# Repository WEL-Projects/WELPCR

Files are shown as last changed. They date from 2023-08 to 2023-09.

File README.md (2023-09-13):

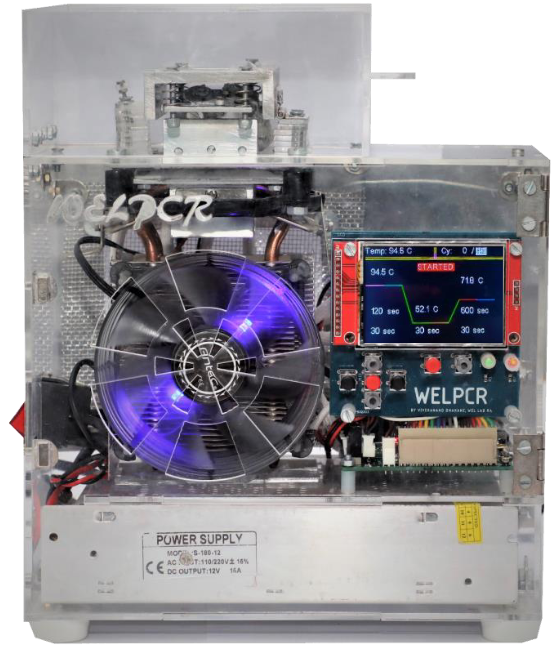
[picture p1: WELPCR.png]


# WELPCR
WELPCR is a low-cost polymerase chain reaction (PCR) thermal cycler for DNA amplification, developed at the [Wadhwani Electronics Lab (WEL)](https://www.ee.iitb.ac.in/~wel_iitb/), [IIT Bombay](https://www.iitb.ac.in/). It is inspired by the [OpenPCR](https://openpcr.org/) design and is a standalone device which does not require connection to a computer or a mobile device for configuration and operation. The bill of materials (BOM) cost for assembling one unit of WELPCR is less than INR Rs. 10,000 (approximately USD $120), which makes it a great resource for educational and research use in laboratories with limited resources. The WELPCR design is open-source and made available for developers interested in assembling their own units.

WELPCR YouTube video: [Watch video](https://www.youtube.com/watch?v=7obOnxuG-sw)

Media article on WELPCR: [Read article](https://www.thehindubusinessline.com/business-tech/affordable-pcr-testing/article65438612.ece)

**If you use this documentation for your project, please cite WELPCR:**

Poulami Mandal*, Vivekanand Dhakane*, Avani Kulkarni, Siddharth Tallur, "WELPCR: Low-cost polymerase chain reaction (PCR) thermal cycler for nucleic acid amplification and sensing," bioRxiv 2023.09.11.557292 (2023). (*equal contribution)

doi: [https://doi.org/10.1101/2023.09.11.557292](https://www.biorxiv.org/content/10.1101/2023.09.11.557292v1)

## Files and folders index
### Folders
Mechanical_design_files: 3D drawings and design files to build the mechanical assembly

PCB: PCB schematic and gerber files for PCR motherboard and display board

STM32_PCR_firmware_for_WELPCR: Firmware for STM32 microcontroller

### Files
Assembly_Instruction.pdf: Step by step guide for assembling WELPCR

MTP PPT.pdf: M.Tech. thesis presentation by Mr. Vivekanand Dhakane

MTP_Report.pdf: M.Tech. thesis report by Mr. Vivekanand Dhakane

Validation document WELPCR.pdf: Protocols for operating WELPCR

WELPCR.png: Photograph of fully assembled WELPCR machine

WELPCR_Temperature_Protocol.pdf: Temperature profile for WELPCR for 16s universal primers

WEL_PCR_BOM.xlsx: Bill of materials (BOM) for WELPCR

WEL_PCR_User_manual.pdf: User manual for operating WELPCR

## Credits
Design and development: Vivekanand Dhakane

Testing and validation: Avani Kulkarni

Documentation and training: Poulami Mandal

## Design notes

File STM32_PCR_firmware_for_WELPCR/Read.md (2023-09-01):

Download stm32 cube ide version 1.6.1
This file[en.st-stm32cubeide_1.6.1_9958_20210326_1446_x86_64.exe]

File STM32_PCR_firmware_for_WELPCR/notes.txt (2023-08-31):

*For lid heater it is found that when PWM 35% then temp is constant at 100 degree
current was nearly 0.85A

*when mosfet is driven by 3.3v
	temperature set =50 degree
		
		if fan not turned on heat sink .its temp = 80
		if fan turned on heat sink .its temp = 56

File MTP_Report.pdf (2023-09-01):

# Low-cost electrochemical sensing

# platform for DNA analysis

### M.Tech Thesis

Submitted in partial fulfillment of the requirements for the degree of

Master of Technology
Solid State Devices (EE7)

by

### Vivekanand Ramrao Dhakane

(193079041)

Under the guidance of

### Prof. Siddharth Tallur

Department of Electrical Engineering, Indian Institute of Technology - Bombay, Powai, Bombay 400076.
June, 2022.

# Thesis Approval

The Thesis entitled

### Low-cost electrochemical sensing platform for DNA analysis

by

Vivekanand Ramrao Dhakane
(193079041)

is approved for the degree of Master’s of Technology in the Department of Electrical Engineering

Prof. Siddharth Tallur
Department of Electrical Engineering (Supervisor)
Prof. Mukul Chandorkar | Prof. Swaroop Ganguly
Department of Electrical Engineering | Department of Electrical Engineering
(Examiner/Chairperson) | (Examiner)

Prof. Debjani Paul
Department of Biosciences and Bioengineering (Examiner)

Date: June 29, 2022
Place: Mumbai.

ii

# Declaration

I declare that this written submission represents my ideas in my own words, and where other ideas or words have been included, I have adequately cited and referenced the original sources. I also declare that I have adhered to all principles of academic honesty and integrity and have not misrepresented, fabricated, or falsified any idea/data/fact/source in my submission. I understand that any violation of the above will cause disciplinary action by the Institute or from whom proper permission has not been taken when needed.

Vivekanand Ramrao Dhakane
(193079041)

June 29, 2022

iii

# Acknowledgement

First and foremost, I am extremely grateful to Prof. Siddharth Tallur for his invaluable advice, continuous support, and patience throughout this project. I am grateful for the constant support and immense help from Maheshwar Mangat Sir in circuit and PCB designing and Mahesh Bhaganagare Sir for helping me in purchasing, and issuing the components from the WEL lab. I am thankful to my colleagues Ruchira Nandeshwar and Shruti Ahuja for their help during the testing of WELStat and Avani Kulkarni for the testing of WELPCR. I would like to thank Mr Vishwas Kewle, Senior Mechanic in Machine tools lab, Mechanical dept for fabricating the heat block and aluminum bracket. I would also like to thank Rutuja Chalke, illustrator in the WEL lab to help me with the PCR illustrations. I would like to express my sincere gratitude to WEL lab authorities for allowing me to use their facilities. I appreciate the constant support from the WEL lab staff, Sadanand sir, Suraj sir, Amit sir, Shanin sir, Shekhar sir and Varsha ma’am. I always had project related brainstorming with my friends Saurabh Thakur, Sarvesh Kale, Omkar Phadke and Jay Jadhav. Finally, I am forever grateful for the encouragement, patience, and support from my parents. Without their tremendous understanding in the past few years, it would be impossible for me to complete this project. I could not have done any of this without them. Thank you all.

Vivekanand Ramrao Dhakane
(193079041)

iv

# Abstract

The ongoing COVID-19 pandemic has highlighted the need for sensitive and cost-effective diagnostics. The gold standard test to diagnose COVID-19 is real time PCR and although there have been multiple advances in PCR testing, the real time PCR thermocyclers are bulky and expensive. Given that PCR is one of the most sensitive and specific testing methods for diagnosis, it is necessary to find a solution to make it affordable especially for low middle income countries(LMICS). This led to the objective of this project to develop a low-cost, portable, and automated real time PCR device. This project includes WELPCR (portable thermocycler), and WELStat (potentiostat that can be connected to a smartphone for electrochemical measurements). The user has to add PCR master mix to pre-processed samples and place them in the holder on WELPCR. The temperature profile and other parameters can be visualized on the LCD display. An electroless nickel immersion (ENIG) PCB electrode is immersed in the PCR sample tubes to note the electrochemical measurements for real-time quantification.

v

# Contents

1 Introduction | 1
2 WELPCR | 4
3 WELStat 2.0 | 22
3.8.1 | End point PCR testing using WELPCR + WELStat . . . . | 32
Appendices | 36

vi

A WELPCR User Manual | 36
B Design Files | 40

vii

# List of Figures

2.4 (a) WELPCR designed in CAD tool Autodesk fusion 360 (b) Actual

2.6 (a) Raw Aluminium block (b) Tube holder after manufacturing (c) bracket after manufacturing (d) Eppendorf tube (e) modified drill bit 8 2.7 (a) 2D parts in WELPCR (b) 2mm aluminium sheet under laser

2.10 (a) Proportional and controller derivative, (b) PD vs PID controller,
(c) Removal of overshoot to get final PID controls, (d) PCR temper-

2.11 Plot showing temperature difference between tube holder and sample 15 2.12 (a) Insulation layer (VHB tape) applied on the tube holder (b) Plot

2.13 (a) Nichrome heater (b) Internal structure of Nichrome heater . . . 16 2.14 (a) Condensation observed in 0.5ml tubes, (b) Tubeholder redesigned

2.15 Comparison of time response for 1mm, 2mm and 5mm thermistor . 17 2.16 (a) Thermistor connected in voltage divider, (b)Set-up for calibrating

viii

2.18 Agarose gel showing 503bp fragment of bacteriophage Phi6 after 35 cycles amplified using WELPCR. NTC is the negative sample and
PC is the positive sample | 19
2.19 Current vs number of cycles plot showing decrease in current with
increase in cycles. Inset showing micro-electrode inserted in the tube | 20
3.1 Working of the Potentiostat, case-I, case-II, and case-III | | 23
3.2 (a) WELSTAT designed in Computer Aided Design tool Autodesk
Fusion 360, (b) WELSTAT after manufacturing | 24
3.3 (a) AD5941, (b) functional block diagram of AD5941 (taken from its
datasheet | 25
3.4 (a)Testing AD5941 on evaluation board, (b) Cyclic Voltammetry plot
for 50µM Methylene blue on AD5941 Evaluation-board | | 26
3.5 STM32F103C8PC IC | | 26
3.6 First PCB for testing minimal circuit for AD5941 | | 27
3.7 Second PCB with both AFE and micro-controller on same board . . | 28
3.8 WELStat software GUI | | 28
3.9 (a)USB wire touching the the electrode wire, (b) Using long wire to connect the electrode, (c) connecting electrode on PCB, (d) IV plot
for 1Mohm when USB wire was touching the the electrode wire (e)
IV plot for 1Mohm when long wire was used to connect the electrode,
(f) IV plot for 1Mohm when electrode was directly connected on PCB 32 3.10 Cyclic voltammetry plot for different concentrations of Methylene
Blue | 33
3.11 Cyclic voltammetry plot for 503bp fragment of Phi6 amplified after 35 cycles using WELPCR and electrochemically detected using WELSTAT. NC is the no-template control, PC is the positive control 33
3.12 H-brige using 4 discrete MOSFET and VNH2SP30 IC | | 35
A.1 (a)PCR parameter window, (b) PCR parameter monitor window . . | 36
A.2 Details about the PCR parameter window | | 37
A.3 Details about the PCR parameter monitor window | | 38
A.4 Front panel of WELPCR | | 38
B.1 Drawing for laser cutting | | 40
B.2 Tube holder drawing | | 41
B.3 Aluminium Bracket drawing | | 42

ix

B.4 WELStat schematic | | 43
B.5 PCR motherboard schematic sheet 1/2 | | 44
B.6 PCR motherboard schematic sheet 2/2 | | 45

x

# List of Tables

2.1 List of challenges faced during designing | 14
2.2 Specification of WELPCR and Comparison with OpenPCR and MiniPCR 21
3.1 Specifications of WELStat | | 24
3.2 Differences between AD5941 and EMStat Pico | | 24
3.3 Data string format from software to controller | | 29

xi

# Chapter 1

# Introduction

The need for accurate, sensitive and low cost diagnostics was sky rocketed during the COVID-19 pandemic. Although there are multiple other rapid technologies for diagnosing infectious diseases such as antigen-antibody based detection, or biochemical assays, they lack the sensitivity and specificity offered by the gold-standard RT-PCR tests. While performing molecular diagnosis it is not possible to detect only a few copies of genomic DNA or RNA. Polymerase chain reaction (PCR) amplifies millions to billion copies of target DNA quickly and accurately which can be studies in greater detail.PCR is a temperature controlled device that cycles between three different temperatures for short period of times. It is essential to maintain these temperatures accurately ensuring a faster transition time between these temperatures to have a faster overall turn around time of the reaction. To develop a PCR device it is essential to consider the need for accurate heating and temperature sensing requirements in such a way that the device is low-cost and not bulky. There have been multiple recent advances in designing portable real time thermocyclers, for instance a group of researchers at the University of Central Florida, Orlando, USA, have developed a 3D- printed real time PCR device operated using battery for diagnosing infectious diseases [1]. The thermal processing and real time fluorescence based detection is controlled by a closed loop feedback and a microcontroller. Multiple open source PCR devices are available such as the Chai Open qPCR that has been used for water monitoring and detecting malarial parasites from blood [2][3]. Despite the advances and open source PCR designs available on the internet, the existing thermocyclers require exhaustive assembling of the design, have relatively lower ramp rates (≤ 1

◦C/s) resulting in longer timescales to

complete a reaction of approximately 35-40 cycles.
After the amplification of target DNA the detection and quantification in a laboratory is usually done using agarose gel electrophoresis. Quantification using agarose gel electrophoresis is end-point detection and is not feasible for on-field or point of care detection. For real-time detection of amplified fragments either optical or electrochemical sensors are used.
In this work, we have tried to make a portable real time PCR device using electrochemical sensing method with minimal need of assembling. The Peltier heater gives a ramp rate of (≤ 2

◦C/s) resulting in a shorter turnaround time. For detection

of the amplicons using electrochemical methods such as cyclic voltammetry we have designed a portable potentiostat, ’WELSTAT’, that can be connected to a smartphone or laptop. The designed PCR device can be used an indispensable tool for multiple application such as forensics, isolation of genomic nucleic acid and testing its purity, detection and classification of organisms, genomic cloning, genotyping, detection of resistant genes, mutation screening, detection of single nucleotide polymorphism, population morphism, gene expression studies, genomic analysis and sequencing and so on.

## 1.1 Motivation

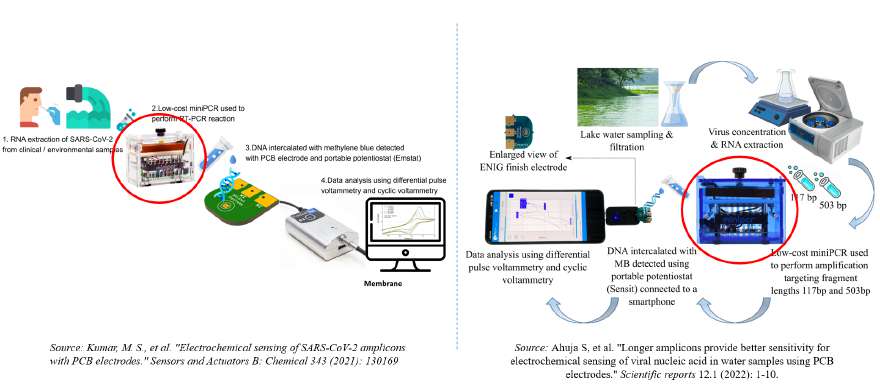
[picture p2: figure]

Figure 1.1: Work done in AIMS lab, EE, IITB

The group I am associated with at AIMS lab, EE, IITB have successfully detected SARS-CoV-2 [4] and bacteriophage Phi-6 [5] from wastewater samples using PCB based electrochemical sensing. While testing the samples, amplification was performed using the MiniPCR thermocycler. The device costs around $800-

1000+shipping charges (imported from US). We faced several maintenance and

2

service issues on the PCR device while performing experiments. This led to the motivation of designing a PCR device that can be used for virus (or any pathogen) detection using electrochemical sensing.For electrochemical sensing they have used PalmSens potentiostat Sensit and EMSTAT Blue. Although the potentiostat is portable with a user-friendly software, we decided to develop a low-cost potentiostat that could serve our purpose of end-point and real-time PCR.

## 1.2 Objectives

- Develop a low-cost, portable, user-friendly PCR device
- Provisions for simultaneous testing of multiple samples (¿ 8 wells)
- Ramp rate (> 1.5°C/s) similar to commercially available PCR device
- Develop a low-cost Potentiostat to perform electrochemical measurements

(Cyclic Voltammetry)

The two main aspects of this thesis include a PCR device (WELPCR) and a potentiostat (WELSTAT). The detailed specifications and design of these two devices are discussed in following two chapters.

3

# Chapter 2

# WELPCR

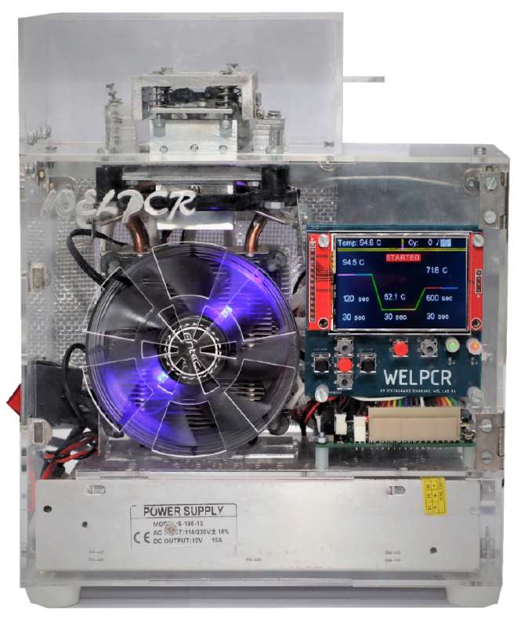
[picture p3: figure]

Figure 2.1: WELPCR

4

WELPCR is a PCR (Polymerase Chain Reaction) machine made by taking OpenPCR [6] as a reference. The main improvement made in WELPCR with respect to OpenPCR is that WELPCR is a standalone device and does not require external device like computer or mobile to configure it. Also it us designed for real-time electrochemical measurements.

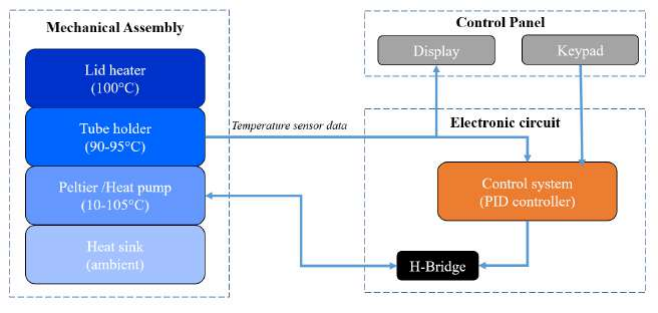
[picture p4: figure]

Figure 2.2: WELPCR block diagram

Figure 2.2 Main part in the mechanical assembly is the peltier. Peltier is basically a heat pump. If current flows in forward direction, it draws heat from heat sink and the tube holder is heated and if current flows in reverse direction then heat is drawn from the tube holder and tube holder is cooled down. Peltier requires bidirectional current so we are using H-bridge. To change and maintain the temperature to different set points PID controller is used. For user interface the control panel consists of display and keys.

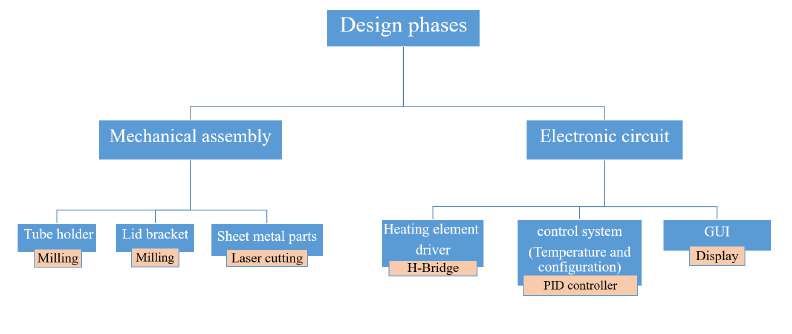
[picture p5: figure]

Figure 2.3: Design phases of WELPCR

The whole design of WELPCR was divided into 2 parts. The first one is Me-

5

chanical Assembly that was finished in Phase-I of this project and the second is Electronic circuit that was completed in this semester. The mechanical assembly includes manufacturing the tube holder, lid bracket and sheet metal parts. Tube holder and lid bracket are 3d parts which are manufactured using milling technique in our Machines and tools lab, Mechanical department, IITB. For 2 dimensional parts were manufacture from aluminium sheet metal. Metal laser cutting facility available at Bhandup was used for sheet metal cutting.
The electronic circuit includes heating element driver, control system for temperature and GUI. As peltier is driven by bi-directional current, H-bridge with driving capacity of 15A is used to drive it. H-Bridge is a is a circuit which allows to pass bi-directional current from the load. Circuit used for H-bridge is given at the top right of the figure B.6. H-bridge has two PMOS and two N-MOS which are IRF9540 and IRF540 respectively.

## 2.1 The Mechanical Structure of the PCR Ma-

## chine

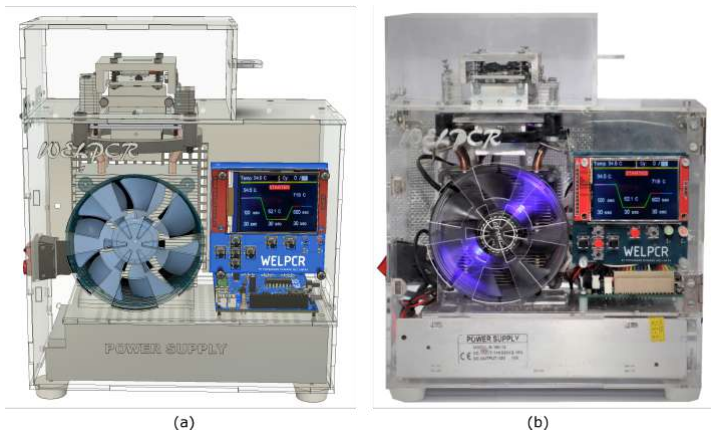
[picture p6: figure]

Figure 2.4: (a) WELPCR designed in CAD tool Autodesk fusion 360 (b) Actual WELPCR after manufacturing

WELPCR has lot of 2D and 3D mechanical parts so it was necessary to design the full system in a Computer Aided Design (CAD) tool in which we can design electronic circuit as well as the mechanical parts. Eagle and Fusion 360 are such

6

CAD tool using which we can design electronic circuit and mechanical parts respectively.Before manufacturing the WELPCR, its model was designed in a CAD tool Autodesk Fusion 360 as shown in figure 2.4. While designing each and every part, care was taken about its Manufacturability, as milling technique has some limitations. Whole assembly is enclosed in a transparent acrylic casing. Acrylic casing is faces are usually fixed with a adhesive. But we need to disassemble the casing many times. So we use the L-bracket with nut-bolt to connect two right angular faces. For maintenance we may need to open one face of the casing. For that, front face is fixed using a hinged on one side. Front of the WELPCR can be opened easily for maintenance purpose.
Figure 2.5 represents the cross-section view of the PCR machine. The CPU cooler is not shown fully.

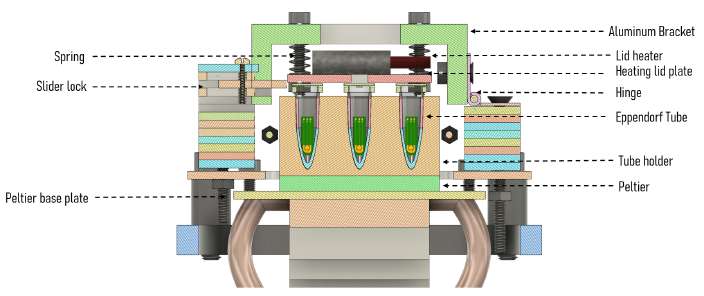
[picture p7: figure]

Figure 2.5: Cross section view of PCR

Following is the description for parts in the above image

- Tube holder: The tube holder is the main part of this PCR. 3 Eppendorf

tubes can be inserted into this block. This block is heated by Peltier.

- Peltier: A Peltier is a heat pump that can pump heat from one side to the

other side depending on the direction of current flow. We can heat and cool the same side just by inverting the supply connections. So both rising and lowering the temperature can be controlled precisely.

- Lid heater: Lid heater is a ceramic 12v 40W ceramic cartridge heater, com-

monly used in 3d printers.

- Heating lid plate: The heating lid plate is heated by a lid heater. This

plate is used to heat the lids of tubes to avoid condensation of liquid sample vapour underneath the tube cap.

7

- Aluminium Bracket: is a solid square bracket ‘[’ shaped lid. This is the

lid that presses the heating lid plate on the lids of the tube. Tension on the heating lid is maintained due to the spring between the bracket and the heating plate.

- CPU cooler: There is no CPU in this PCR machine, but this big heat sink

with a cooling fan is a part of the desktop CPU used for cooling the microprocessor. This CPU cooler is used to sink(while decreasing the temperature) and source(while increasing the temperature) the heat.

- Peltier base plate: Peltier base plate is used as an interface between the

CPU cooler and the Peltier. The shape and area of the Peltier and the CPU cooler are not the same so to collect heat from the whole area of the Peltier and to pass that heat to the CPU cooler, this Peltier base plate is used.

- eppendorf tube: These are tubes made for preparing, mixing, centrifuging,

storing, and transporting solid and liquid reagents and samples. We use 0.2ml eppendorf tubes.

Manufacturing the the 3D parts

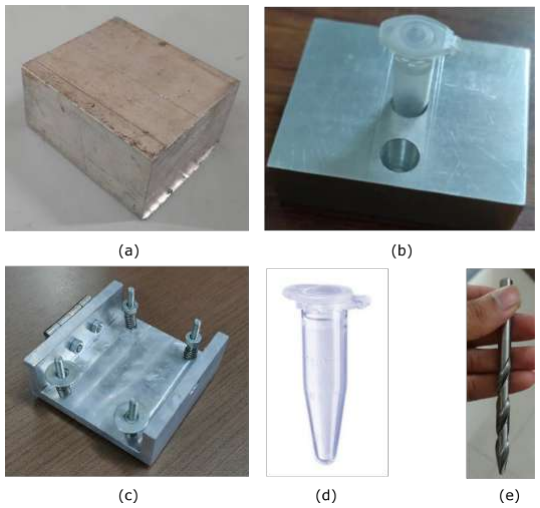
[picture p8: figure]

Figure 2.6: (a) Raw Aluminium block (b) Tube holder after manufacturing (c) bracket after manufacturing (d) Eppendorf tube (e) modified drill bit

8

After designing parts in CAD software fusion 360, we manufactured these parts using milling technique and laser cutting. Milling is machining technique in which we remove the material from workpiece using rotary cutter. 3D parts were manufactured using milling in machine and tools lab, IITB. There are two 3d metal parts in our design, that are tube holder and bracket. Aluminium metal is used for both, as it is light weight and requires less efforts in milling.
Above figure B.1 shows the raw aluminium block (figure B.1(a)), tube holder (figure B.1(b)) and bracket (figure B.1(c)). Actual thermal cycling is performed at the bottom of the tube. So bottom of the tube must in good thermal contact with the tube holder. Eppendort tube shown in figure B.1(d) has a conical shape bottom. The main challenge while manufacturing the tube holder was to make a conical hole for the tube. Because when we make a hole using drill bit it makes a cylindrical hole but we need a conical hole. Outer profile of the drill bit was modified such that it matches with the outer profile of the tube as shown in figure B.1(e)

Manufacturing the the sheet metal parts

There were some 2 dimensional parts in WELPCR design like a heated lid plate, a plate between peltier and heat sink . These parts were manufactured using the metal laser cutting machine.

Figure 2.7: (a) 2D parts in WELPCR (b) 2mm aluminium sheet under laser cutting machine (c) Aluminium sheet after laser cutting

9

## 2.2 PCR Cycle

PCR or Polymerase Chain Reaction is a temperature controlled device. PCR cycles through different temperatures for different time. The first step is denaturation which requires 90-95°C [7] . It causes the denaturation i.e DNA is broken

into double-stranded DNA template as shown in figure 2.8. Second step is annealing which requires 50-60°C. In this step primers is annealed to each of the single-stranded DNA templates. Third step is extension which requires 72°C. In

this step,new DNA strand complementary to the DNA template strand is synthesized. Each cycle doubles the number of DNAs .This cycle is repeated for n number of times. so it multiplies the no. of DNA by 2 raised to n. We need to design a system which cycles through these three steps for n number of times.

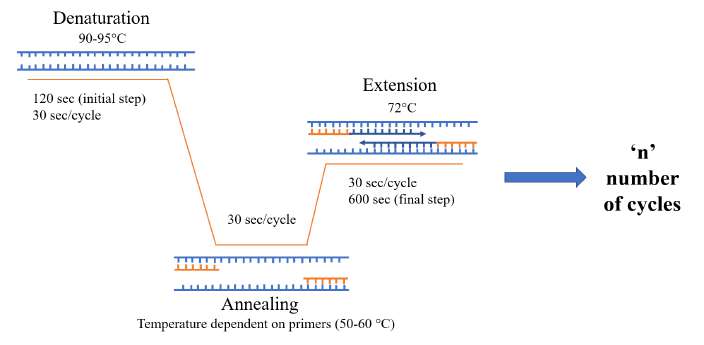
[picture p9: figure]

Figure 2.8: PCR temperature profile for single cycle

Figure 2.9 represents the temperature profile for a single cycle of PCR. The blue curve shows the temperature profile of the tube holder, which is directly attached to the Peltier. An orange curve shows the temperature profile of the sample inside the test tube. The sample temperature is always less than the holder temperature by 1-2 degrees because the sensor measuring the temperature of the holder is closer to the heater. Also, there is heat loss at the interface of the tube and the holder. Heat loss across this interface is minimized by using thermal conducting paste. To measure the temperature, we used a 1 mm 4.7K thermistor. The temperature sensor needs to be as small as possible because the sample is 20ul which fills the test tube just by 2-3 mm, so a big thermistor adds a thermal load and results in heat loss as well as wrong temperature readings because the big thermistor does not dip fully into the sample.

10

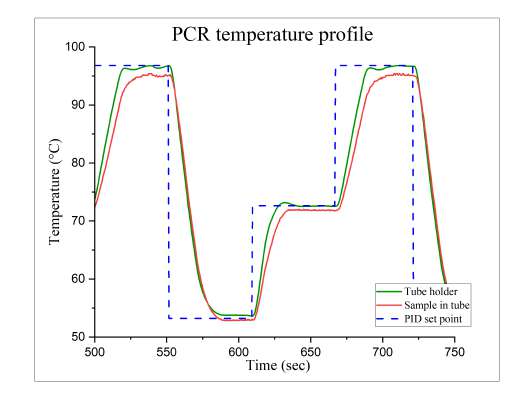
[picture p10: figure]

Figure 2.9: Actual temperature profile of WELPCR

## 2.3 PID controller

In our design, we used Peltier for heating as well as cooling the tube holder. A PID controller is designed to raise the temperature of the tube holder as fast as possible. As PCR is temperature sensitive and primers may be damaged because of overshoot in the temperature, we need a critically damped temperature control system. To achieve this critically damped system, we used the try and error method. Following equation is used for PID

PWM duty cycle = kp × e(t) + kd ×

∂e(t)
∂t + ki ×

R
e(t)dt + β
where :
kp = P roportional gain
kd = Derivative gain
ki = Integral gain
e(t) = Error (difference between set point and current temperature) β = bias depend on the temperature
What is β in PID equation?
To maintain the constant temperature peltier require some constant current bias. This required current bias may change from its calculated value due to the surrounding temperature. For example, We want to set tube holder temperature at 72°C. consider at 50% duty cycle tube holder temperature remain constant at 72°C, then β will be equal to 500 for 72°C. For 50% , β is 500 because we put 1000 in

timer countdown register in micro-controller. value of β is directly proportion to

11 the temperature. equation of β is linear for the range of nearly 10°C. so equation of β is different for 90±5°C, 72±5°C and 56±5°C. Following are the equations for

different temperature ranges of PCR cycle:

β = 8.2 × temperature − 300 | for 51oC < temperature < 61oC
β = 8.5 × temperature − 292 | for 67oC < temperature < 77oC
β = 9.2 × temperature − 345 | for 88oC < temperature < 98oC

If peltier is driven by only βwithout PID controller, there will some constant error in steady stead as the surrounding temperature changes. for example, if surrounding temperature is lower then PWM duty cycle needs to be higher and if surrounding temperature is higher, PWM duty cycle needs to be lower. Three terms of PID takes care of this change in surrounding temperature. Proportional, integral and derivative terms of the PID get added to or substracted from the βdepending on the sign of error.
Now next task is to tune the PID controller. That is to find the kp, ki and kd to get the critically damped system.
Trial and error method to tune the PID
- Increase the kp till we get constant oscillations in the steady state.
- Increase the kd till the oscillation amplitude is within the acceptable range.
- Increase the ki till you get a steady state error in the acceptable range.

Figure 2.10 shows the temperature vs time plot for different PID constants. We can see from the graph Figure 2.10(a) that for kp = 10 we get the oscillations in the steady state. As kd and ki are zero, this is only a proportional controller. To suppress these oscillations, we need to increase the kd. We directly used kd = 70 but it did not have any effect on the oscillations. So we tried kd = 70 and it was increasing the oscillations. So we decreased the kd till 35 and we got the curve as shown in the above graph (green, kp = 10, kd = 35). But still, there is a problem with the PD controller. In a steady state, we can see there is a constant drift in the temperature. To suppress this constant drift, we need to add an integral controller. We get the following curves after adding the integral controller.
Figure 2.10(b) shows the curves with the integral (blue) and without the integral (red) controller. For the PID controller (blue), we can see that temperature is constant in the steady state and steady state error is also within the acceptable

12

Figure 2.10: (a) Proportional and controller derivative, (b) PD vs PID controller,
(c) Removal of overshoot to get final PID controls, (d) PCR temperature profile after PID tuning

range. Still, there is a problem here, and that is the overshoot. This overshoot can damage the chemicals in the test tube, which are temperature sensitive. Overshoot can be decreased by decreasing the integral gain. The following graph shows the effect of decreasing the integral gain.
Figure 2.10(c) shows the response with overshoot with ki = 2 (red) and the critically damped response with ki = 1. We can see there is no overshoot in the critically damped response (blue). Decreasing the ki solved the problem of overshooting. This is how we got our required PID controller response.
The calculated PID constants are valid only for the temperature around 93±5°C.

That is, PID constants change if there is a change in set point. The same method of PID tuning is used to tune the PID controller for the other two set points, which are 55±5°C and 72±5°C. The following plot shows the final PCR cycle.

13

## 2.4 Challenges faced during designing

Challenges | Solution | Remark
tube holder and sample | Insulation of tube holder | Failed Poor heat transfer between
| Additional nichrome coil heater along with Peltier | Failed
Condensation on side walls of tube | Tube holder designed for smaller tubes covering entire tube sidewalls | Successful (Solved poor heat transfer problem too)
Slow time response of the temperature sensor | Use of small 1mm thermistor | Successful
Noise in temperature sensor | Connecting full mechanical assembly to ground of the circuit | Successful
Micro-controller out of stock due to chip shortage | De-soldered microcontroller from old board | Successful
Accurate temperature sensor calibrations | Calculated different equations for each temperature sensor | Successful
Time required for self heating of temperature sensor | Use of smaller 1mm sensor | Successful
Size of temperature sensor larger than sample size | Use of smaller 1mm sensor | Successful
SI2302 MOSFET damage exceeding Pmax of MOSFET | Use of ON/OFF switch instead of PID controller which operates MOSFET in cutoff or linear region | Successful
Damage of power supply due to short circuit | Use of fuse | Successful
Spike in output voltage of supply damaging the controller | Use of Transient Voltage Suppression (TVS) diode | Successful

Table 2.1: List of challenges faced during designing

Poor heat transfer between tube holder and sample

Initially we were using 5ml tube for testing. As side walls of the 5ml tubes are thicker than the 0.2ml tube, it was oberverve that there was difference of 30-40°C

14

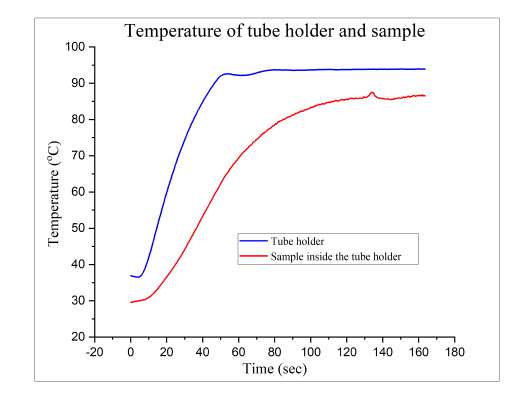
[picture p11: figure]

Figure 2.11: Plot showing temperature difference between tube holder and sample

between tube holder and sample temperature as shown in figure 2.11. to solve this problem we first put same thermal paste at the interface of tube holder and tube, but it did not solved the problem.

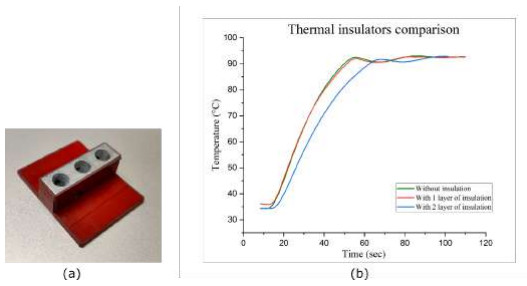
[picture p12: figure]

Figure 2.12: (a) Insulation layer (VHB tape) applied on the tube holder (b) Plot showing curves for different no. layers of insulation

We though that there might be heat loss from outer surface of the tube holder which is causing the poor heat transfer. So we applied the insulator on outer surface of the tube holder. For insulation VHB tape was applied on the outer surface as shown in the figure 2.12 (a). But from the figure 2.12 (b), we can observe, as no. of layers of insulation increases, ramp rate decreases. So, though insulation is preventing the heat loss in steady state, it was decreasing the ramp rate in transition state. So this solution failed.

15 figure 2.12 (b) shows there is huge gap between tube holder and sample temperature. So we decided to raise the temperature of the holder such that we get sample temperature of set point. For example, if we want sample temperature to be 95°C, then increase the temperature to 110-120°C. But the maximum temperature that can be achieved using the peltier is 105°. Also ramp rate is decreases after 80°C so it takes nearly 1.5 minute to reach temperature at 105°C. To solve this problem,

we decided to add one more heater. As only assistance for heating was required we decided to use Nichrome coil for heater. Following figure

Figure 2.13: (a) Nichrome heater (b) Internal structure of Nichrome heater

Condensation

When vapours of liquid find a surface with lower temperature it get settled on that surface in its liquid form. Initially we used 5ml tubes and designed a tube holder for it which was covering only bottom of the tube. Side walls were not covered with by the holder as shown in the Figure 2.14(a). So though temperature of bottom of the tube was near 95°C, side walls were not reaching to such high temperature. It

results in the condensation of the sample on side walls of tubes. This condansation would not have been affected the test if sample quantity was large but sample we put in the tube is just 20µL, which fills just 3mm of tube from bottom. So due to condensation entire 20µL sample leaves the bottom of the tube where actual

thermal cycling is performed. The heated lid prevents condensation under the lid of the tube. Sample droplets, which are condensed on the side wall, do not undergo the PCR reaction. As our sample under the test is just 20µL, condensation will

affect the PCR process.
To solve this problem, we replaced the 0.5ml test tube with a 0.2ml test tube and redesigned the test tube holder to cover the full sidewall of the test tube, as shown Figure 2.14 (b).

16

Figure 2.14: (a) Condensation observed in 0.5ml tubes, (b) Tubeholder redesigned for0.2ml tubes to solve the condensation challenge

Time response of the temperature sensor

Selecting the temperature sensor with faster time response was one of the challange in this project. Initially we tried LM35 as it has linear output and it is already calibrated. But problem with LM35 was it was taking nearly 1 minute to attend high temperature 93°C. It might be due to its our packaging which was causing

slower heat transfer to the actual sensor inside the package. So we were in search of faster temperature sensor which can have time response such at least 2°C/sec.

Figure 2.15: Comparison of time response for 1mm, 2mm and 5mm thermistor

After discarding LM35, we decided to test the thermistor for our application. Learned from the previous mistake this time we plotted time response of different size thermistor. We can see from the above figure 2.15,as the size of thermistor decreases, time response of the thermistor improves. We decided to use 1mm thermistor as its time response was better than 2mm and 5mm thermistors. Also we need to measure the temperature of liquid sample inside the tube. Amount of sam-

17 ple that we use for the PCR is just 20L and it fills just 3mm of the tube from the bottom. so using 2mm or 5mm thermistor add more thermal load in addition to the actual sample. So sensor itself takes time for self heating. Also if sensor is not fully dipped into the sample, it give 3-10°C less reading than the actual. To prevent

such problems 1mm themistor was the best choice among other sensor.

The temperature sensor and its calibration

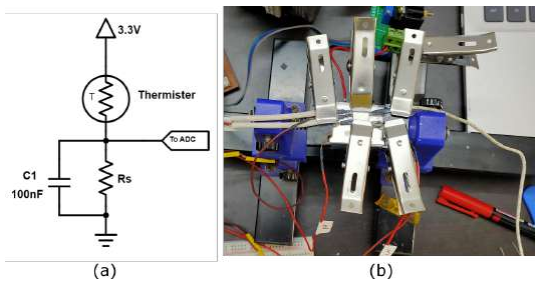
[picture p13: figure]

Figure 2.16: (a) Thermistor connected in voltage divider, (b)Set-up for calibrating the thermistor

Figure 2.16 shows the set-up for calibrating the thermistor. Initially, we were using 10k Ohm thermistor. In circuit diagram ??(a) value of Rs is geometric mean of the resistance values of thermistor for the temperature range and capacitor C1 is 100nF to for noise filtering [8]. For calculating the temperature from the resistance, we used βmodel equation of the thermistor show in the following equation:

R = R0(e

β(

1
T − 1 298.15 )))

βvalue of the thermistor was taken from the datasheet.After some testing, we found that every thermistor has some deviation from its standard β value given in the datasheet. This deviation of the β value results in a deviation of +-3 degrees of temperature, which is very high as PCR is a temperature-sensitive reaction. To solve this problem, we decided to treat every thermistor differently to get a temperature value from it. In firmware, the thermistor library is updated such that it takes a β value of the thermistor when we initialize the structure for a thermistor. To calculate the β value we made a small heater using a nichrome coil. To control the temperature, the current was controlled using the transistor. We took resistance readings for different temperatures. A temperature reading was

18 taken using a standard thermocouple thermometer and a resistance reading was taken using a multimeter. The fixture and setup are shown in the Figure 2.17

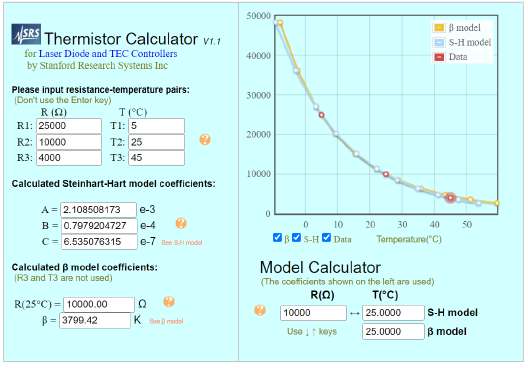
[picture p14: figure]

Figure 2.17: ’Thermistor Calculator’ by Stanford Research System, Inc

After taking readings of resistance for different temperatures, β value was calculated using a ’Thermistor Calculator’ by Stanford Research System, Inc [9] shown in figure 2.17.

## 2.5 WELPCR Results

Figure 2.18: Agarose gel showing 503bp fragment of bacteriophage Phi6 after 35 cycles amplified using WELPCR. NTC is the negative sample and PC is the positive sample

After completing the PCR assembly, we needed to check whether it amplifies RNA or not. For that, we ran 35 cycles of PCR for a 503bp fragment of Phi6 bacteriophage. The Phi6 bacteriophage is a commonly used surrogate for SARS-CoV-2,

19 which is non-infectious and has a lipid envelope similar as the virus responsible for Covid-19. After running PCR for 35 cycles, amplification was verified using agarose gel electrophoresis . As shown in figure 2.18, we can see the dark band for the positive sample (sample with the virus) and no band for the negative sample (sample without virus). The intensity of band is proportional to the amount of the amplified DNA.

### 2.5.1 Real-time sensing using EMStat Potentiostat

Real-time PCR refers to the detection of amplicons in real-time, i.e, as they are amplifying during the PCR reaction. This saves time and cost of power requirements to run a specific number of cycle depending on the pathogen. We use WELPCR for amplification and dipped in unmodified PCR electrodes in the reaction tubes for real-time sensing using PalmSens EMStat Potentiostat. The DNA intercalating redox dye was added along with PCR master mix reagents before starting the reaction and not at the end of the reaction with an additional one hour of incubtion. As seen in Figure 2.19, there is no change in the peak current for the No-template control (NTC) with increase in number of PCR cycles. Whereas, for the positive control we sea clear decline in the peak current with increase in the number of PCR cycles. It can be clearly seen that the positive control can be distinguished from the negative control at the 12th PCR cycle. This result concludes that WELPCR can be combined with an electrochemical sensor in order to achieve

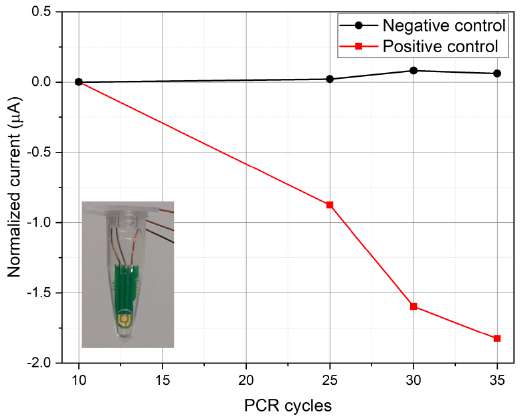
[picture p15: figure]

Figure 2.19: Current vs number of cycles plot showing decrease in current with increase in cycles. Inset showing micro-electrode inserted in the tube

20

## 2.6 WELPCR Comparison

WELPCR is inspired from the openPCR [6]. We improved lot of features in WELPCR. WELPCR has a higher ramp rate almost double of openPCR. Reverse transcription can be performed using WELPCR, and other devices except MiniPCR.Currently we have manufactured a sample holder for 9 tubes that can be customized later to have more number of wells. User interface (read as given in the boxes). Our device weighs 1.9 kg which can be reduced, that is discussed in future improvements. The Bill of material price of our device is less than 10000. Following table shows comparison of WELPCR with openPCR and MiniPCR

| WELPCR | OPENPCR | MiniPCR mini8
Max Ramp rate | 2 ◦C/s | 1 ◦C/s | 2.4 ◦C/s
Reverse transcription | Yes | No | No
Wells | 9 | | 8
Temperature range | 10-105◦C | 20-105◦C | Ambient-99◦C
User Interface | Keys+Touch
| screen Display

Computer Software Mobile App

Weight | 1.9kg | | 0.45kg
Heated lid | Yes | Yes | Yes
Cost | Rs. 10,000 (BOM) | Rs. 38,500 (BOM) | Rs. 75,000 + shipping
| | | from USA and taxes

Table 2.2: Specification of WELPCR and Comparison with OpenPCR and MiniPCR

21

# Chapter 3

# WELStat 2.0

In last chapter, we have seen details about the WELPCR. WELPCR is used for DNA amplification i.e making copies of DNA. Sample under the test don’t have the amount of DNA that is detectable by the sensor. After amplification using PCR our next task is to detect the DNA. This detection can be done by electrochemical method using WELStat. WELStat is a potentiostat designed in the Wadhawani Electronics Lab (WEL). Now lets see what is a potentiostat?

## 3.1 What is a Potentiostat?

Potentiostat is a essential tool in electrochemical research used for applying the potentiostat and measuring the current. It can do so while keeping the path where the current flows separate from the path where the potential is measured. Now lets see why do we need to separate the voltage and current measurement loop. Consider we want to plot a current vs voltage plot for a electrolyte. We take that electrolyte in a beaker and dipped two electrodes. To change the voltage between two electrode a variable voltage supply is connected. To measure the current we have connected the ammeter. After connected all of these components our setup will look like as shown in the case-I of figure 3.1. We are interested in measuring the voltage of one electrode only that is called the working electrode and another electrode is called the counter electrode.

Consider case-I, at t=0, potential drop at both the electrode is same i.e V1/2 . Now in case-II, after passing some time, the rate of reaction on both the electrode are different. So potential on both electrode changes with times. So the voltage of working electrode measured by the voltmeter will not be correct as it is measured

22

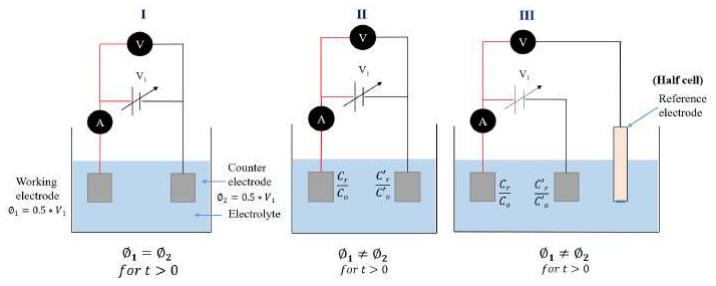
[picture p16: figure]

Figure 3.1: Working of the Potentiostat, case-I, case-II, and case-III

with respect to varying reference that is counter electrode. To measure the actual voltage of the working, it must be measured with respect to some constant voltage. So in case-III, we introduced third electrode i.e reference electrode. Reference electrode is a half cell whose potential remain constant irrespective of concentration of the electrolyte or time. In case-III, ground of the voltmeter is connected to the reference. So we are measuring the current passing from loop working electrode
- counter electrode - V1/2 and voltage of working electrode is measured with respect to reference electrode. In this way, the loop we are measuring the current is separated from loop in which the voltage is measured.

## 3.2 WELStat

WELStat 2.0 shown if Figure 3.2 is an improved version of WELStat 1.0. WELStat 1.0 was made with discrete electronic components such as Opamp, ADC, DAC etc. So the previous version required a large PCB which was creating concerns about its portability and power too. In this version i.e. WELStat 2.0, we used Analog Front End (AFE) IC AD5941 IC which has two potentiostats inbuilt and there is no need for any external peripherals except some capacitors and resistors.

## 3.3 Specifications

Specifications of the WELStat are listed in following table.

23

Figure 3.2: (a) WELSTAT designed in Computer Aided Design tool Autodesk Fusion 360, (b) WELSTAT after manufacturing

Parameter
Excitation voltage range | -1.2 to +2 V
Max current | ±3mA
ADC | 16 bit
DAC | 12bit
No. of Potentiostat | 2
No. of channels | 1

Table 3.1: Specifications of WELStat

AD5941 | EMStat Pico
Price = 700 | Price = 45,000
Needs an external micro-controller | Micro-controller + Potentiostat
Not pre-programmed | Pre-programmed
Programing using embedded-C language | human-readable scripting language for ease of programming

Table 3.2: Differences between AD5941 and EMStat Pico

Choosing Analog Front End IC (AFE)

We wanted to make our device as compact as possible. So instead of building potentiostat using discrete components, we decided to use the potentiostat IC that is Analog Front End (AFE) IC. There are multiple potentiostat ICs available. Two of these are AD5941 and EMStat.Both are manufactured by analog devices. Table 3.2 and table 3.1 differences and similarities respectively in AD5941 and EM-

24

Stat Pico respectively. Both have similar specifications but their price difference is huge. AD5941 costs around Rs.700 and EMStat pico for Rs.45000. Although both EMSTAT Pico and AD5941 have almost similar specifications, the high-cost of EMSTAT Pico is mainly due to the well designed user-friendly software and accurately calibrated potentiostat.so we wanted to try if AD5941 can be used for our application.

AD5941

The AD5941[10] are high precision, low power Analog Front End (AFEs) designed for portable applications that require high precision, electrochemical-based measurement techniques, such as amperometric, voltammetric, or impedance measurements. This AFE has a sequencer that is specifically designed for offloading the AFE operations from external micro-controllers. It can be configured and data can be read from it using SPI protocol.

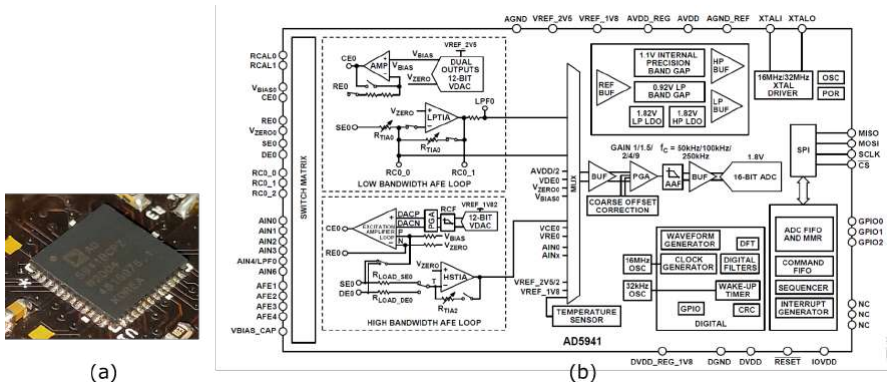
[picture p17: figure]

Figure 3.3: (a) AD5941, (b) functional block diagram of AD5941 (taken from its datasheet

Figure 3.3 shows the overall block functional block diagram of AD5941. There are two types of potentiostat in the block diagram, indicated by ‘LOW BAND-WIDTH AFE LOOP’ and ‘HIGH BANDWIDTH AFE LOOP’. In most of our applications, we are going to use ‘LOW BANDWIDTH AFE LOOP’ which is also called Low Power (LP) potentiostat. It can measure the current from 50 pA to 3mA. For excitation, it has a 12-bit Digital to Analog Converter (DAC). For measuring current, the current is converted to voltage using the Trans-Impedance Amplifier (TIA). This output voltage of TIA is measured by Analog to Digital Converter(ADC). This

25 measured voltage is proportional to the input current to TIA. The proportionality constant is decided by the gain of the TIA which is programmable. This ADC data can be read by the micro-controller instantly or this data can be stored in the inbuilt FIFO and then read once the applied excitation wave is completed.

Testing AD5941

To test whether AFE AD5491 is suitable for our application or not, we tested it using an off the shelf evaluation board as shown in Figure 3.4 (a). After achieving fair results (Figure 3.4(b))on the evaluation board of AD5941, we decided to use it for our application.

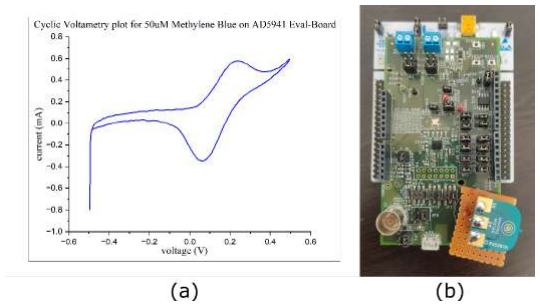
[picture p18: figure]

Figure 3.4: (a)Testing AD5941 on evaluation board, (b) Cyclic Voltammetry plot for 50µM Methylene blue on AD5941 Evaluation-board

STM32 Micro-controller

Figure 3.5: STM32F103C8PC IC

As shown in Figure 3.5 STM32F103C8T6 [11] is used as a host micro-controller.

26

For configuring AFE, requirements from the host micro-controller are: it should have SPI, UART communication protocols and at least 64kb of flash memory.

## 3.4 First PCB

Figure 3.6: First PCB for testing minimal circuit for AD5941

Figure 3.6 represents a red board mounted on the whiteboard. The whiteboard is a Nucleo board. The red board is designed for the minimal circuit of the AFE IC. So this version of the AFE PCB, i.e. red PCB, has only the AFE IC on it. The micro-controller is on a Nucleo board. This board was designed just to test the minimal circuit requirement for AFE IC. This circuit was tested using a 30 mM ferrocyanide solution and then compared with commercially available potentiostat. Figure... represents the CV plot for that. We got a similar shape but there is some shifting x as well as the y axis. We are still working on finding the reason behind it.

## 3.5 Second PCB

As seen in the first PCB, there was only AFE IC. While making the second PCB we planned to make a single PCB for AFE as well as micro-controller STM32. So this second circuit is nothing but a combination of the first PCB and a Nucleo board. As seen in Figure 3.7, the left male USB port is connected to the USB pins of the STM32 micro-controller. The right side female USB port is for the USB electrode. A three-pin header near the male USB port with the jumper is used to select the 5v supply source, i.e whether to take 5V from the male USB port or the UART to USB converted port (golden colour thermal tape). Four pin header in the above PCB is used by the ST-Link programmer to program the micro-controller

27

Figure 3.7: Second PCB with both AFE and micro-controller on same board

STM32 which is mounted on the bottom side of the PCB. Figure... represents good cathodic and anodic peaks with respect to commercially available PalmSens Sensit Smart potentiostat.

## 3.6 WELStat Software

### 3.6.1 GUI: Overview

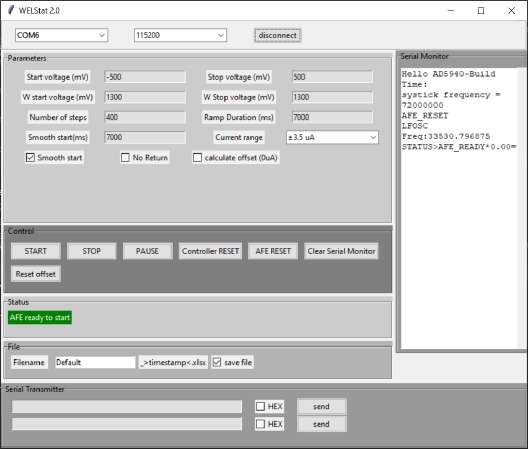
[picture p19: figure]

Figure 3.8: WELStat software GUI

28

WELStat Software figure 3.8 is a program used for configuring WELStat and then plotting the graph of the data collected from the WELStat via UART. This GUI is made using python language.
It stores the data in .xlsx format i.e. excel file. Once it has all the data points, it automatically plots the data. Also, it has the feature to plot multiple graphs in a single plot. Following are some of the shortcuts.
- ctrl+f : select spreadsheet
- ctrl+a : plot graph
- ctrl+x : clear
- ctrl+s : save all graphs in on spreadsheet

### 3.6.2 DATA String formats

From Software to the controller : datatype>parameter*value=

datatype [10] | Parameter [15] | Default value [10]
COM (command) | RAMP START | 0
COM (command) | RAMP STOPNOW | 0
COM (command) | RAMP STOPSYNC | 0
COM (command) | RAMP SHUTDOWN | 0
COM (command) | RESET(AFE reset) | 0
COM (command) | RESET(AFE reset) | 0
COM (command) | CONTROLLERRESET | 0
CHG (parameter change) | RampStartVolt | ±1300
CHG (parameter change) | RampPeakVolt | ±1300
CHG (parameter change) | bRampOneDir | 0 or 1
CHG (parameter change) | VzeroStart | 1300
CHG (parameter change) | VzeroPeak | 1300
CHG (parameter change) | StepNumber | 400
CHG (parameter change) | RampDuration | 7+
CHG (parameter change) | Smoothstart | 1
CHG (parameter change) | LPTIARtiaSel | 0-26

Table 3.3: Data string format from software to controller

29

- COM>RAMPSTART*0=
- COM>RAMPSTOPSYNC*0=
- COM>RAMPSTOPNOW*0=
- COM>RAMPSHUTDOWN*0=
- COM>RESET*0=
- CHG>bRampOneDir*1=
- CHG>RampPeakVolt*300=
- CHG>StepNumber*300=
- CHG>RampStartVolt*-200=
- CHG>RampDuration*10000=]

From controller to Software datatype>parameter*value=

30

## 3.7 Challenges faced during designing

Challenges | Solution | Remark
Soldering QFN and QFP package ICs | Self-learnt soldering QFN and QFP package ICs | Successful
Porting the example program given by the manufacturer for STM32 controller | Converted the program given for STM32F411 to STM32F103 | Successful
Electromagnetic interference (EMI) | Care taken while PCB designing to minimize electrode track length as small as possible. No signal carrying track should be near the electrode tracks. | Successful
Every time connector needs to be soldered on electrode | USB male connector directly printed on electrode | Successful
Real-time electrochemical sensing of PCR amplicons | Need for further calibration of a potentiostat and make it Noise-proof | Future scope

Problems while testing AD5941 evaluation board

AD5941 was easy for getting started as example codes were given for different applications like amperometry and cyclic voltammetry. But we were not getting noise free results for the current for the order of 1mA and lower. To test the AD5941 board we plotted current vs voltage plot for 1 Mohm resistor. We observed a lot of noise in cyclic voltammetry plots as shown in figure 3.9(d). This noise was due to the Electromagnetic interference (EMI) of the nearby clock or data carrying wires, for example, USB wire connected to the computer shown in figure 3.9(a). Electromagnetic interference or EMI is a unwanted interference or noise due to external sources. So we tested the board by separating the electrode wire from other wires as shown in figure 3.9(b). It reduced the noise to some extent as shown in the figure 3.9(e) but still the plot is noisy. So to avoid long wire, we used a port

31

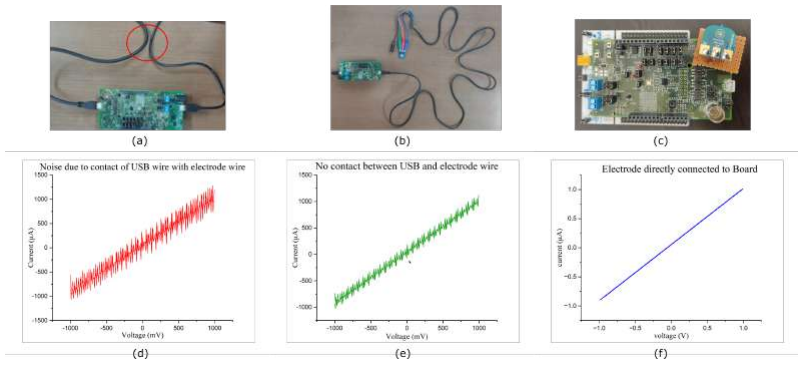
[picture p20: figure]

Figure 3.9: (a)USB wire touching the the electrode wire, (b) Using long wire to connect the electrode, (c) connecting electrode on PCB, (d) IV plot for 1Mohm when USB wire was touching the the electrode wire (e) IV plot for 1Mohm when long wire was used to connect the electrode, (f) IV plot for 1Mohm when electrode was directly connected on PCB

given on the board nearer to the AD5941 IC and we did not see any noise that we can see in the Figure 3.9 (f). Learning from this we decided to minimize the distance between electrodes and AD5941 IC while PCB designing.
To make electrode connection more simple and free from the external components like male and female headers, we decided to use a USB type A female port on AFE PCB and the electrode itself will be a USB type A male port. The only thing that needs to be remembered while using a USB male port printed on a PCB is that the thickness of the PCB must be 2mm.

## 3.8 WELStat Results

Figure 3.10 is the cyclic voltammetry plot plot for different concentration of Methylene blue using WELStat. As we can see in the graph with increase in MB concentration there is an increase in current.

### 3.8.1 End point PCR testing using WELPCR + WELStat

After verifying that our WELPCR amplifies the sample successfully by agarose gel electrophoresis, we wanted to check whether the amplification could be detected using our potentiostat, WELStat. We did the same procedure as before. That

32

Figure 3.10: Cyclic voltammetry plot for different concentrations of Methylene Blue

is, running 35 PCR cycles for the 503bp fragment of bacteriophage Phi6. After PCR, this time instead of testing amplification using gel electrophoresis, we checked amplification by plotting a cyclic voltammetry plot using the WELStat.

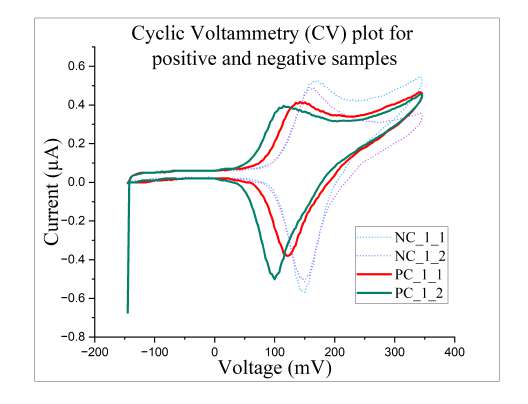
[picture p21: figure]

Figure 3.11: Cyclic voltammetry plot for 503bp fragment of Phi6 amplified after 35 cycles using WELPCR and electrochemically detected using WELSTAT. NC is the no-template control, PC is the positive control

For electrochemical measurements, we need to add methylene blue (MB), which is a redox indicator dye that intercalates DNA. If the sample is positive, amplified DNA or RNA gets intercalated with the MB, resulting in a deacrease as well as

33 shifting of the peaks in the CV plot.
To check the repeatability of the result, we plotted the CV plot for three different samples of Phi6 bacteriophage whose PCR was done at different times. From the figure 3.11, we can see the decrease and shifting of the peaks. The decrease in peak current indicates amplification of the target DNA or RNA.

34

## 3.9 Future improvements

- Using H-bridge IC: Current WELPCR is over-designed so size of the WELPCR

can be reduced. The MOSFETs used in the current device require a big heat sink thereby occupying more space. These MOSFET, gate driver and heat sink can be replaced by VNH2SP30, which is an H-bridge motor driver IC to reduce the overall size of the device.

Figure 3.12: H-brige using 4 discrete MOSFET and VNH2SP30 IC

- Use of smaller heat-sink for peltier: Current WELPCR use a big heat

sink for peltier. After some testing it was found that such a big heat-sink is not requires for the peltier. Smaller heat-sink with size 50% smaller than the current heat-sink.

- Protection circuit: While testing the WELPCR, peltier was damaged due

to the overcurrent. So we can have a high current protection circuit before the peltier port.

- Smaller version of WELPCR: Current WELPCR size is big just because

of the big 15A power supply. Such high current rating power supply is required just to get the high temperature ramp rate. So we can have a smaller version of WELPCR which will have slower ramp rate so it will require smaller power supply. This PCR will be optimized for the size instead of the ramp rate

- Real-time testing using the WELStat: In real time electrochemical sens-

ing the is lot of noise due to PWM which drives the peltier. So we need to reduce noise in WELSTAT to perform the Real-time electrochemical PCR.

35

# Appendix A

# WELPCR User Manual

### A.0.1 User Interface

Figure A.1: (a)PCR parameter window, (b) PCR parameter monitor window

As shown in Figure A.1 WELPCR has a 2.4” touch screen 240x320 display. The display has two windows. The first window is the ‘PCR Parameter Window,” and the second window is the ‘PCR Parameter Monitor Window’. In the PCR parameter window, we can see the current parameters of the single PCR cycle, which are temperature and time for denaturation, annealing, and extension. These parameters can be selected and changed by the navigation keys. The second window, the ’PCR Parameter Monitor Window’, is for monitoring the live parameters.
PCR parameter window:
1. The total number of cycles
2. The number of cycles completed
3. Extension temperature
4. Extension time for the last cycle

36

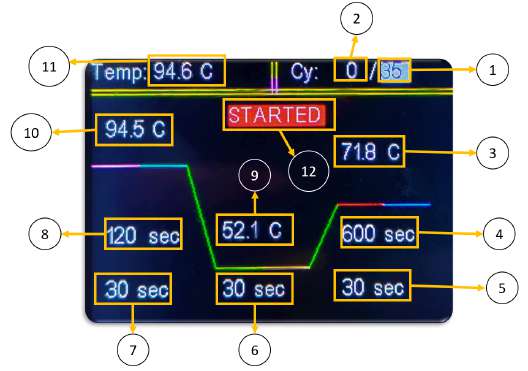
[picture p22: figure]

Figure A.2: Details about the PCR parameter window

5. Extension time of a single cycle
6. Annealing time
7. denaturation time
8. Initial denaturation temperature
9. Annealing temperature
10. Denaturation temperature
11. the current temperature of the tube holder
12. ‘STARTED’ or ‘STOPPED’ indicates the current state of PCR.

PCR parameter monitor window:

1. The number of cycles completed
2. The total number of cycles
3. The current set point of the PID controller
4. Percentage progress of the current PCR test
5. Time remaining for the current PCR test.
6. Temperature measured by the temperature sensor probe

37

Figure A.3: Details about the PCR parameter monitor window

7. Temperature measured by the temperature sensor probe 2.
8. Temperature of the heated lid
9. Current Ramp rate
10. Current tube holder temperature

PCR front panel

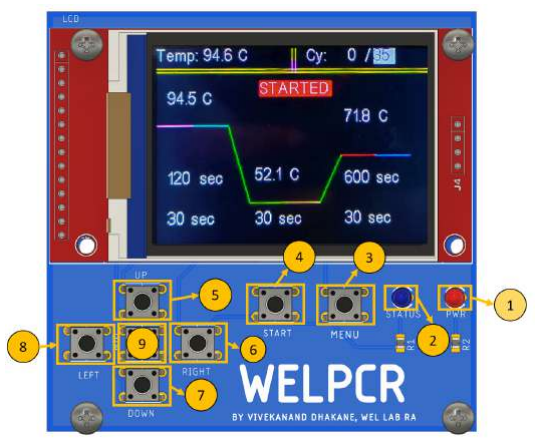
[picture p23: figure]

Figure A.4: Front panel of WELPCR

1. Power LED

38

2. Status LED
3. MENU: To change the window
4. START: Long press to start or stop the test.
5. UP: Shift the cursor up.
6. RIGHT: Shift the cursor right.
7. Down: Shift the cursor down.
8. LEFT: Shift the cursor left.
9. MID: Select the parameters.

Procedure

On PCR Parameter Window, navigate using the navigation keys. Select the parameter to be changed using the MID-button and adjust it using the navigation key. UP and DOWN keys change the parameter by 0.1 if it is temperature and change it by 1 if it is time. LEFT and RIGHT buttons change the parameters by 10. Once parameters are set, long-press the START button to start the test. The status on the screen will be changed to STARTED Change the window using the MENU button to see real-time parameters like remaining time and percentage progress. Once the test is completed, the status on the screen will be changed to STOPPED.

Important points to remember while testing

If we want to plot the temp of the sample, the temperature sensor must be fully dipped in the sample. While taking real time reading using WELStat or any other potentiostat, the ground of the measuring instrument must be connected to the ground of the PCR or body of the PCR (as the PCR body is connected to the ground of the PCR).

39

# Appendix B

# Design Files

Figure B.1: Drawing for laser cutting

40

Figure B.2: Tube holder drawing

41

Figure B.3: Aluminium Bracket drawing

42

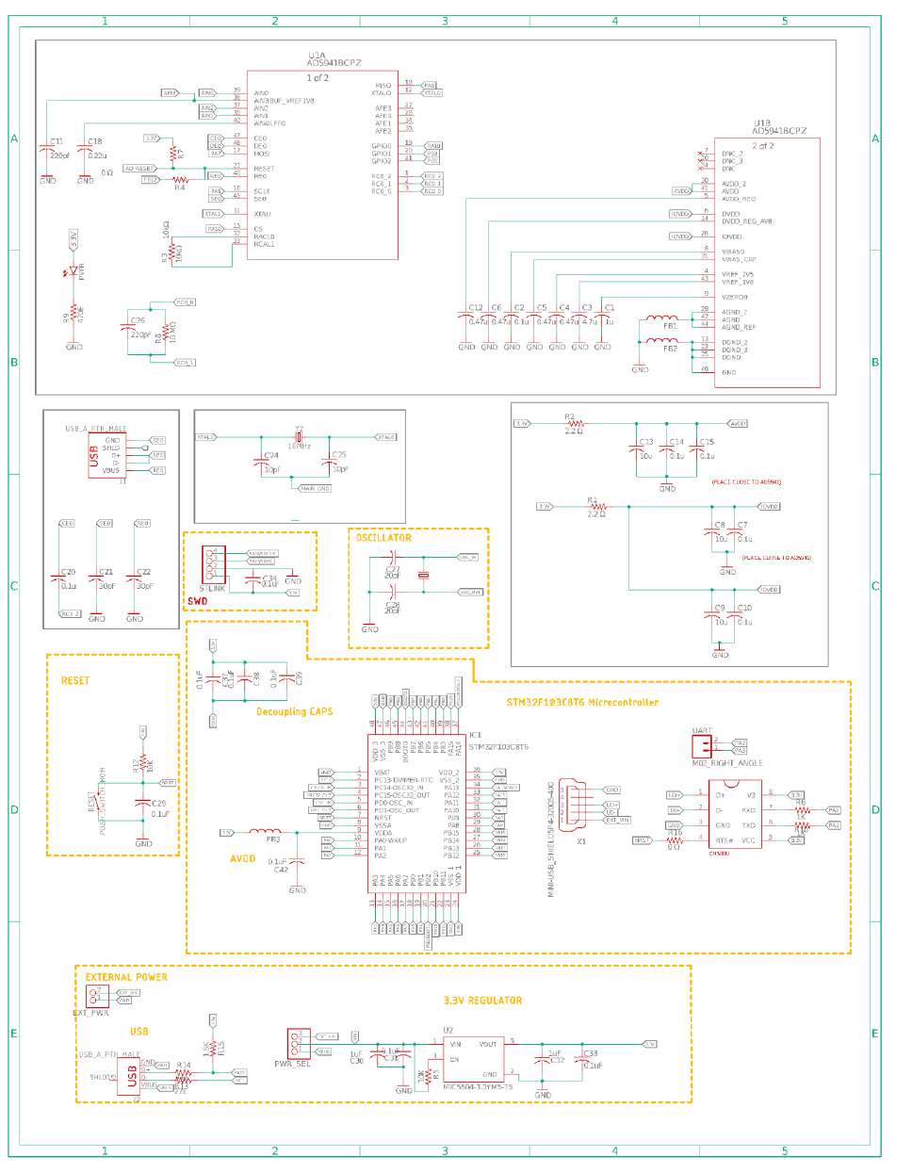
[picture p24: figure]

Figure B.4: WELStat schematic

43

Figure B.5: PCR motherboard schematic sheet 1/2

44

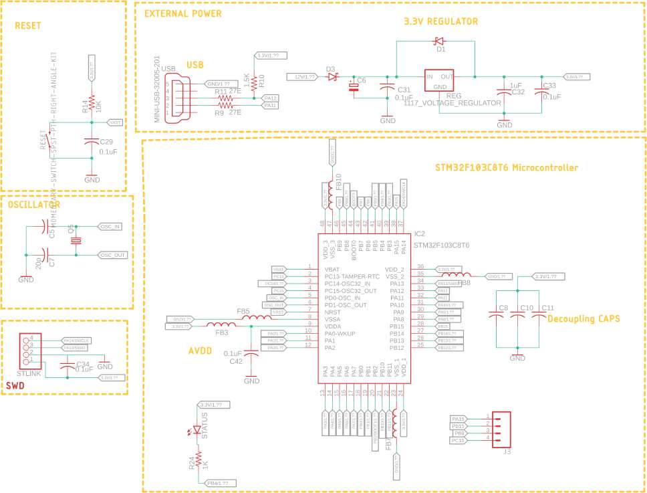
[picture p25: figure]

Figure B.6: PCR motherboard schematic sheet 2/2

45

# Bibliography

[1] Geoffrey Mulberry, Kevin A White, Manjusha Vaidya, Kiminobu Sugaya, and Brian N Kim. 3d printing and milling a real-time pcr device for infectious disease diagnostics. PLoS One, 12(6):e0179133, 2017.
[2] Sydney P Rudko, Ronald L Reimink, Bradley Peter, Jay White, and Patrick C Hanington. Democratizing water monitoring: Implementation of a communitybased qpcr monitoring program for recreational water hazards. PloS one, 15(5):e0229701, 2020.
[3] Brian J Taylor, Kjerstin Lanke, Shanna L Banman, Isabelle Morlais, Merribeth J Morin, Teun Bousema, Sanna R Rijpma, and Stephanie K Yanow. A direct from blood reverse transcriptase polymerase chain reaction assay for monitoring falciparum malaria parasite transmission in elimination settings. The American journal of tropical medicine and hygiene, 97(2):533, 2017.
[4] MS Kumar, Ruchira Nandeshwar, Shailesh B Lad, Kirti Megha, Maheshwar Mangat, Adrian Butterworth, Charles W Knapp, Mara Knapp, Paul A Hoskisson, Damion K Corrigan, et al. Electrochemical sensing of sars-cov-2 amplicons with pcb electrodes. Sensors and Actuators B: Chemical, 343:130169, 2021.
[5] Shruti Ahuja, M Santhosh Kumar, Ruchira Nandeshwar, Kiran Kondabagil, and Siddharth Tallur. Longer amplicons provide better sensitivity for electrochemical sensing of viral nucleic acid in water samples using pcb electrodes. Scientific reports, 12(1):1–10, 2022.
[6] Chai Biotechnologies. Openpcr: The $ 499 opensourcepcrmachine/thermalcy-

cler. 2018.

[7] Polymerase chain reaction. https://www.ncbi.nlm.nih.gov/pmc/articles/PMC4102308/. (https://www.ncbi.nlm.nih.gov/pmc/articles/PMC4102308/) Accessed: 2022-06-20.

46

[8] Texas Instruments. Monitoring ntc thermistor circuit with single-ended adc. Analog Engineer’s Circuit: Data Converters, SBAA338–March 2019.
[9] ’thermistor calculator’ by stanford research system. https://www.thinksrs.

com/downloads/programs/therm20calc/ntccalibrator/ntccalculator. html. (https://www.thinksrs.com/downloads/programs/therm20calc/ntccalibrator/ntccalculator.html) Accessed: 2022-03-20.

[10] Analog Devices. | High precision, impedance, and electrochemical front
end ad5940/5941. | Data Sheet.[Online]. Available: https://www. analog.
com/media/en/technical-documentation/data-sheets/AD5940-5941. pdf, 2020.
[11] Warren Gay. Stm32f103c8t6 gpio pins. In Beginning STM32, pages 393–400. Springer, 2018.

47

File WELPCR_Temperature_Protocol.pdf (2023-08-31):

WEL-PCR TEMPERATURE PROTOCOL FOR 16S UNIVERSAL PRIMERS

Device-WELPCR

WEL, Electrical Engineering Department Indian Institute of Technology Bombay


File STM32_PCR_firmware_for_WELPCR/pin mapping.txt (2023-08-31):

A8 - Timer1 - ch1 - PWM - peltier
A9 - Timer1 - ch2 - PWM - peltier
A10- Timer1 - ch3 - PWM - lid heater
A0 - ADC0 - Block temp
A1 - ADC1 - Lid temp
A2 - ADC2 - Extra 1
A3 - ADC3 - Extra 2

A4 - buzzer
B4 -Status

B0  - UP
B1  - Down
B10 - Left
B11 - Right
B12 - Mid
B13 - Set
B14 - RST

SPI
A5-CLK
A6- MISO
A7-MOSI
C14- LCD_cs
B2 - DC
B5 - LCD reset

B3 - Touch CS
B8 - Touch IRQ

I2C
B7 - SDA
B6 - SCK

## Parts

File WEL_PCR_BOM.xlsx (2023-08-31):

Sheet: PCB
 | Length | Width | Quantity | Price |  | Quantity | Price
 |  |  |  | 7WD | 10WD |  | 10WD
Motherboard(mm) | 92 | 71 | 4 | 3380 | 3276 | 3 | 2998
DisplayBoard(mm) | 78.7 | 77.1 | 4 | 3299 | 3200 | 3 | 2945
Total |  |  |  | 6679 | 6476 |  | 5943

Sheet: BOM_All
To be ordered | Ordered | Available in lab | Received order | May be in lab | issued
Component | Price of single piece | Quantity required for Single ckt | Price | product link | Quantity for 2 piece | Quantity to be ordered | Price for order | Comment
IRF540/530 | 25 | 2 | 50 | robu (https://robu.in/product/irf540n-to-220-3-mosfet-pack-of-2-ics/) | 4 | 6 | 150
IRF9540/9530 | 35 | 2 | 70 | EC (https://www.electronicscomp.com/irf9540n-100v-23a-p-channel-power-mosfet-to-220-package?search=IRF%209540) | 4 | 6 | 210
STM32F103C8 | 756 | 1 | 756 | shravi (https://sharvielectronics.com/product/stm32f103c8t6-arm-microcontroller-lqfp-48-package/) | 2 | 3 | 2268
2.4 inch TFT display | 743 | 1 | 743 | robu (https://robu.in/product/2-4-inch-spi-interface-240x320-touch-screen-tft-colour-display-module/) | 2 | 3 | 2229
antec a30 cpu cooler | 1001 | 1 | 1001 | amazon (https://www.amazon.in/Antec-Cpu-Cooler-Fan-Compatible/dp/B01HLAHDWE) | 2 | 2 | 2002
tube holder material | 100 | 1 | 100 | - | 2 | 2 | 200
tube holder machining | 500 | 1 | 500 | - | 2 | 2 | 1000
lid bracket material | 100 | 1 | 100 | - | 2 | 2 | 200
lid bracket machining | 500 | 1 | 500 | - | 2 | 2 | 1000
12v 10A power supply | 690 | 1 | 690 | EC (https://www.electronicscomp.com/12v-10amp-smps-dc-metal-power-supply-nwp-india?search=12v%2010A%20power%20supply) | 2 | 2 | 1380
8Mhz crystal | 9 | 1 | 9 | EC (https://www.electronicscomp.com/8mhz-crystal-oscillator-hc49-us-package?search=8Mhz%20crystal) | 2 | 3 | 27
USB Mini-B SMD Connector | 18 | 1 | 18 | https://zbotic.in/product/kls1-229-5fb-mini-usb-connector-type-b-2-0-pcb-mount-right-angle-smd/ | 2 | 3 | 54
PCR mother board | 900 | 1 | 900 | PCB Power | 2 | 2 | 1800
L293D | 30 | 1 | 30 | EC (https://www.electronicscomp.com/index.php?route=product/search&search=L293) | 2 | 3 | 90
PCR display board | 900 | 1 | 900 | PCB Power | 2 | 2 | 1800
XT60 male Connector | 13.5 | 2 | 27 | ET (https://etstore.in/index.php/product/xt60-male-connectors/) | 4 | 6 | 81
XT60 Female Connector | 14 | 2 | 28 | ET (https://etstore.in/index.php/product/xt60-female-connectors/) | 4 | 6 | 84
buzzer | 13.5 | 1 | 13.5 | ET (https://etstore.in/index.php/product/5v-buzzer-cedicom-active-magnetic-long-continous-beep-tone-129-5mm/) | 2 | 3 | 40.5
~~12v 40W Ceramic Cartridge Heater~~ | ~~78~~ | ~~1~~ | ~~78~~ | ~~Robo~~ (https://robocraze.com/products/12v-40w-ceramic-cartridge-heater?currency=INR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) | ~~2~~ | ~~3~~ | ~~234~~
M7 diode | 2 | 1 | 2 |  | 2 | 3 | 6
15A peltier | 340 | 1 | 340 | https://www.electronicscomp.com/tec1-12715-thermoelectric-15a-peltier-cooler-generator-module | 2 | 3 | 1020
ST link | 649 | 1 | 649 | Amazon | 2 |  | 0
Male to Female Jumper | 1.2 | 10 | 12 | ET (https://etstore.in/index.php/product/1-piece-jumper-wires-female-to-male-20cm-length/) | 20 |  | 0
male to male Jumper | 1.3 | 10 | 13 | ET (https://etstore.in/index.php/product/1-piece-jumper-wires-male-to-male-20cm-length/) | 20 |  | 0
Female to Female Jumper | 1.1 | 10 | 11 | ET (https://etstore.in/index.php/product/1-piece-jumper-wires-female-to-female-20cm-length/) | 20 |  | 0
16 Pin RMC male | 8.4 | 1 | 8.4 | ET (https://etstore.in/index.php/product/16-pin-rmc-relimate-connector-2-54mm-male/) | 2 | 3 | 25.2
16 Pin RMC Female with wire | 24 | 1 | 24 | ET (https://etstore.in/index.php/product/16-pin-rmc-relimate-connector-male-female-1-pair/) | 2 | 3 | 72
2mm thermistor | 15 | 2 | 30 | Micro Impex, Grant Road | 4 |  | 0
L- bracket | 5 | 20 | 100 | vegakit, Grant road | 40 | 50 | 250 | Bhandup
M3 6mm bolt | 1.35 | 70 | 94.5 | Abinson (https://www.abinson.com/1010) | 191 | 150 | 202.5 | Bhandup
M3 nut | 0.6 | 108 | 64.8 | Abinson (https://www.abinson.com/1014) | 216 | 300 | 180 | Bhandup | 191
m3 30mm bolt | 5 | 4 | 20 | Mangaldeep | 8 | 12 | 60 | Bhandup
M3 22mm bolt | 5 | 4 | 20 |  | 8 | 12 | 60 | Bhandup
M5 nut | 5 | 4 | 20 |  | 8 | 12 | 60 | Bhandup
M5 25mm bolt | 5 | 4 | 20 |  | 8 | 12 | 60 | Bhandup
M3 15mm bolt | 1 | 6 | 6 |  | 12 | 18 | 18 | Bhandup
M3 40mm bolt | 1 | 4 | 4 |  | 8 | 12 | 12 | Bhandup
m3 20mm bolt | 4 | 4 | 16 |  | 8 | 12 | 48 | Bhandup
~~m3 nyloc nut~~ | ~~4~~ | ~~4~~ | ~~16~~ |  | ~~8~~ | ~~12~~ | ~~48~~ | ~~Bhandup~~
3 Pin RMC Female | 5.12 | 4 | 20.48 | ET (https://etstore.in/index.php/product/3-pin-rmc-relimate-connector-male-female-1-pair-copy/) | 8 | 10 | 51.2
3 Pin RMC male | 1.35 | 4 | 5.4 | ET (https://etstore.in/index.php/product/3-pin-rmc-relimate-connector-male/) | 8 | 10 | 13.5
hinge 23mm x 25mm | 6 | 4 | 24 | Mangaldeep | 8 | 10 | 60 | Bhandup
Acrylic sheet 2 ft x 2ft | 400 | 1 | 400 | Offline | 2 |  | 0
silicon red | 2.54 | 2 | 5.08 | sunrom (https://www.sunrom.com/p/red-soft-silicone-switch-cap) | 4 | 6 | 15.24
silicon black | 2.54 | 2 | 5.08 | sunrom (https://www.sunrom.com/p/black-soft-silicone-switch-cap) | 4 | 6 | 15.24
silicon white | 2.54 | 2 | 5.08 | sunrom (https://www.sunrom.com/p/transparent-soft-silicone-switch-cap) | 4 | 6 | 15.24
Tactile Switch 6x6x18mm | 5.9 | 7 | 41.3 | sunrom (https://www.sunrom.com/p/tactile-switch-6x6x18mm) | 14 | 20 | 118
~~Tactile Switch 6x6x17mm~~ | ~~5.9~~ | ~~7~~ | ~~41.3~~ | ~~sunrom~~ (https://www.sunrom.com/p/tactile-switch-6x6x17mm) | ~~14~~ |  | ~~0~~
1117 3.3v voltage regulator | 13 | 1 | 13 | EC (https://www.electronicscomp.com/ams1117-3.3v-voltage-regulator-smd-sot-23-package-india) | 2 |  | 0
Nichrome Wire (5 m) | 169 | 1 | 169 | Amazon (https://www.amazon.in/dp/B07H2LYXHN?ref=ppx_pop_mob_ap_share) | 1 | 1 | 169 | Bhandup
Mica Sheets | 142 | 1 | 142 | Amazon (https://www.amazon.in/dp/B08K4F82D3?ref=ppx_pop_mob_ap_share) | 1 | 1 | 142 | Bhandup
12v 555 DC Motor | 653 | 1 | 653 | Amazon (https://www.amazon.in/dp/B09765X5B1?ref_=cm_sw_r_apan_dp_X6YPGNSAGDWME76DH26S) | 1 | 1 | 653
Mica Sheet (small)
 |  |  | 9508.92
Value | Device | Quantity required for Single ckt
Value is not given | SCHOTTKY-DIODESMD | 2
0.1uF | C-USC0603 | 5
1.5K | R-US_R0805 | 1
10K | R-US_R0603 | 1
10k | R-US_R0805 | 5
~~1117_VOLTAGE_REGULATOR~~ | ~~1117_VOLTAGE_REGULATOR~~ | ~~1~~ | ~~3.3,1.8 , 33V available in lab~~
1K | R-US_R0603 | 1
1k | R-US_R0805 | 6
1uF | C-USC0603 | 1
20p | C-USC0805 | 1
27E | R-US_R0805 | 2
 | L293D | 1
 | LED_RED_0805 | 1

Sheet: BOM_Motherboard_set1
Part | Value | Device | Package | Description | ARROW_PART_NUMBER | ARROW_PRICE-STOCK | DESCRIPTION | HEIGHT | MANUFACTURER_NAME | MANUFACTURER_PART_NUMBER | MF | MOUSER_PART_NUMBER | MOUSER_PRICE-STOCK | MPN | OC_FARNELL | OC_NEWARK | POPULARITY | PROD_ID | SF_SKU | SPICEPREFIX
#ERROR! | SCREW_TERMINAL_5.08 | SCREW_TERMINAL_5.08 | SCREW_TERMINAL_5.08
 | Not to be soldered |  | Done |  | Not available |  | Available
12V | WIREPAD4
BLOCK_TEMP |  | CONN_03 | 1X03 | Multi connection point. Often used as Generic Header-pin footprint for 0.1 inch spaced/style header connections
BUZ | BUZ | BUZZER-PTH | BUZZER-12MM | Buzzer |  |  |  |  |  |  |  |  |  |  |  |  |  | COMP-08253 | COM-07950
C1 |  | C-USC0805 | C0805 | CAPACITOR
C2 |  | C-USC0805 | C0805 | CAPACITOR
C3 |  | C-USC0805 | C0805 | CAPACITOR
C4 |  | C-USC0805 | C0805 | CAPACITOR
C5 | 20 pf | C-USC0805 | C0805 | CAPACITOR
C6 | 1uf | CPOL-EUE5-5 | E5-5 | POLARIZED CAPACITOR
C7 | 20pf | C-USC0805 | C0805 | CAPACITOR
C8 | 1uf | C-USC0805 | C0805 | CAPACITOR
C9 |  | C-USC0805 | C0805 | CAPACITOR
C10 | 1uf | C-USC0805 | C0805 | CAPACITOR
C11 | 1uf | C-USC0805 | C0805 | CAPACITOR
C12 | 1mf | CPOL-EUE5-5 | E5-5 | POLARIZED CAPACITOR
C13 | 100uf | C-USC0805 | C0805 | CAPACITOR
C14 | 100uf | C-USC0805 | C0805 | CAPACITOR
C15 | 100uf | C-USC0805 | C0805 | CAPACITOR
C16 | 100uf | C-USC0805 | C0805 | CAPACITOR
C29 | 0.1uF | C-USC0603 | C0603 | CAPACITOR
C31 | 0.1uF | C-USC0603 | C0603 | CAPACITOR
C32 | 1uF | C-USC0603 | C0603 | CAPACITOR
C33 | 0.1uF | C-USC0603 | C0603 | CAPACITOR
C34 | 0.1uF | C-USC0603 | C0603 | CAPACITOR
C42 | 0.1uF | C-USC0603 | C0603 | CAPACITOR
D1 | ss14 | SCHOTTKY-DIODESMD | SMB | Schottky Diode |  |  |  |  |  |  |  |  |  |  |  |  | 2
D3 | ss14 | SCHOTTKY-DIODESMD | SMB | Schottky Diode |  |  |  |  |  |  |  |  |  |  |  |  | 2
EX1_TEMP |  | CONN_03 | 1X03 | Multi connection point. Often used as Generic Header-pin footprint for 0.1 inch spaced/style header connections
EX2_TEMP |  | CONN_03 | 1X03 | Multi connection point. Often used as Generic Header-pin footprint for 0.1 inch spaced/style header connections
FAN |  | CONN_03 | 1X03 | Multi connection point. Often used as Generic Header-pin footprint for 0.1 inch spaced/style header connections
FB3 |  | FERRITE-BEADA | 603 | Ferrite beads in various packages
FB5 |  | FERRITE-BEADA | 603 | Ferrite beads in various packages
FB7 |  | FERRITE-BEADA | 603 | Ferrite beads in various packages
FB8 |  | FERRITE-BEADA | 603 | Ferrite beads in various packages
FB10 |  | FERRITE-BEADA | 603 | Ferrite beads in various packages
GND | WIREPAD4
IC1 | L293D | L293D | DIL16 | PUSH-PULL 4 CHANNEL DRIVER |  |  |  |  |  |  |  |  |  | L293D | 9589619 | 56P8249 | 16
IC2 | STM32F103C8T6 | STM32F103C8T6 | QFP50P900X900X160-48N | Mainstream Performance line
J1 |  | CONN_16 | 1X16 | Multi connection point. Often used as Generic Header-pin footprint for 0.1 inch spaced/style header connections
J3 |  | F04_LOCKLOCK | F04_LOCK | Multi connection point. Often used as Generic Header-pin footprint for 0.1 inch spaced/style header connections |  |  |  |  |  |  |  |  |  |  |  |  |  | CONN-09696
JP1 | JUMPER-SMT_2_NC_PASTE_SILK | JUMPER-SMT_2_NC_PASTE_SILK | SMT-JUMPER_2_NC_PASTE_SILK | Normally closed solder jumper
JP2 | JUMPER-SMT_2_NC_PASTE_SILK | JUMPER-SMT_2_NC_PASTE_SILK | SMT-JUMPER_2_NC_PASTE_SILK | Normally closed solder jumper
LID_HEATER | SCREW_TERMINAL_5.08 | SCREW_TERMINAL_5.08 | SCREW_TERMINAL_5.08
LID_TEMP |  | CONN_03 | 1X03 | Multi connection point. Often used as Generic Header-pin footprint for 0.1 inch spaced/style header connections
PWR | LED_RED_0805 | LED_RED_0805 | RED_LED
Q1_N | IRF530 | IRF530 | TO220BV | HEXFET Power MOSFET |  |  |  |  |  |  |  |  |  |  |  |  | 2
Q2_P | IRF9530 | IRF9530 | TO220BV | P-CHANNEL HEXFET POWER-MOS-FET |  |  |  |  |  |  |  |  |  |  |  |  | 4
Q3_P | IRF9530 | IRF9530 | TO220BV | P-CHANNEL HEXFET POWER-MOS-FET |  |  |  |  |  |  |  |  |  |  |  |  | 4
Q4_N | IRF530 | IRF530 | TO220BV | HEXFET Power MOSFET |  |  |  |  |  |  |  |  |  |  |  |  | 2
Q5 |  | CRYSTALHC49S | HC49/S | CRYSTAL |  |  |  |  |  |  |  |  |  |  | 1667008 | unknown | 49
R1 | 10k | R-US_R0805 | R0805 | RESISTOR
R2 | 1k | R-US_R0805 | R0805 | RESISTOR
R3 | 1k | R-US_R0805 | R0805 | RESISTOR
R4 | 1k | R-US_R0805 | R0805 | RESISTOR
R5 | 1k | R-US_R0805 | R0805 | RESISTOR
R6 | 10k | R-US_R0805 | R0805 | RESISTOR
R7 | 10k | R-US_R0805 | R0805 | RESISTOR
R8 | 10k | R-US_R0805 | R0805 | RESISTOR
R9 | 27E | R-US_R0805 | R0805 | RESISTOR
R10 | 1.5K | R-US_R0805 | R0805 | RESISTOR
R11 | 27E | R-US_R0805 | R0805 | RESISTOR
R12 | 1k | R-US_R0805 | R0805 | RESISTOR
R13 | 1k | R-US_R0805 | R0805 | RESISTOR
R14 | 10K | R-US_R0603 | R0603 | RESISTOR
R15 | 10k | R-US_R0805 | R0805 | RESISTOR
R24 | 1K | R-US_R0603 | R0603 | RESISTOR
REG | 1117_VOLTAGE_REGULATOR | 1117_VOLTAGE_REGULATOR | SOT230P700X180-4N
RESET | MOMENTARY-SWITCH-SPST-PTH-RIGHT-ANGLE-KIT | MOMENTARY-SWITCH-SPST-PTH-RIGHT-ANGLE-KIT | TACTILE_SWITCH_PTH_RIGHT_ANGLE_KIT | Momentary Switch (Pushbutton) - SPST |  |  |  |  |  |  |  |  |  |  |  |  |  | CONN-10672 | COM-10791
STATUS |  | LEDCHIP-LED0603 | CHIP-LED0603 | LED |  |  |  |  |  |  |  |  |  |  |  |  | 26
STLINK |  | PINHD-1X4 | 1X04 | PIN HEADER |  |  |  |  |  |  |  |  |  |  |  |  | 91
SUPPLY_OUT | M02_RMC | M02_RMC | M02_RMC
U1 | SI2302 | SI2302 | SOT95P240X110-3N
USB | MINI-USB-32005-201 | MINI-USB-32005-201 | 32005-201 | MINI USB-B Conector |  |  |  |  |  |  |  |  |  |  | unknown | unknown | 5
TVS DIODE | 12 v

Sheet: BOM_Motherboard_set2
Qty | Value | Device | Package | Parts | Description | ARROW_PART_NUMBER | ARROW_PRICE-STOCK | DESCRIPTION | HEIGHT | MANUFACTURER_NAME | MANUFACTURER_PART_NUMBER | MF | MOUSER_PART_NUMBER | MOUSER_PRICE-STOCK | MPN | OC_FARNELL | OC_NEWARK | POPULARITY | PROD_ID | SF_SKU | SPICEPREFIX
13 |  | C-USC0805 | C0805 | C1
5 |  | CONN_03 | 1X03 | BLOCK_TEMP
1 |  | CONN_16 | 1X16 | J1 | Multi connection point. Often used as Generic Header-pin footprint for 0.1 inch spaced/style header connections
2 |  | CPOL-EUE5-5 | E5-5 | C6
1 |  | CRYSTALHC49S | HC49/S | Q5 | CRYSTAL |  |  |  |  |  |  |  |  |  |  | 1667008 | unknown | 49
1 |  | F04_LOCKLOCK | F04_LOCK | J3 | Multi connection point. Often used as Generic Header-pin footprint for 0.1 inch spaced/style header connections |  |  |  |  |  |  |  |  |  |  |  |  |  | CONN-09696
5 |  | FERRITE-BEADA | 603 | FB3
1 |  | LEDCHIP-LED0603 | CHIP-LED0603 | STATUS | LED |  |  |  |  |  |  |  |  |  |  |  |  | 26
1 |  | PINHD-1X4 | 1X04 | STLINK | PIN HEADER |  |  |  |  |  |  |  |  |  |  |  |  | 91
2 |  | SCHOTTKY-DIODESMD | SMB | D1
5 | 0.1uF | C-USC0603 | C0603 | C29
1 | 1.5K | R-US_R0805 | R0805 | R10 | RESISTOR
1 | 10K | R-US_R0603 | R0603 | R14 | RESISTOR
5 | 10k | R-US_R0805 | R0805 | R1
1 | 1117_VOLTAGE_REGULATOR | 1117_VOLTAGE_REGULATOR | SOT230P700X180-4N | REG |  | 3.3,1.8 , 33V available
1 | 1K | R-US_R0603 | R0603 | R24 | RESISTOR
6 | 1k | R-US_R0805 | R0805 | R2
1 | 1uF | C-USC0603 | C0603 | C32 | CAPACITOR
1 | 20p | C-USC0805 | C0805 | C7 | CAPACITOR
2 | 27E | R-US_R0805 | R0805 | R9
1 | BUZ | BUZZER-PTH | BUZZER-12MM | BUZ | Buzzer |  |  |  |  |  |  |  |  |  |  |  |  |  | COMP-08253 | COM-07950
2 | IRF530 | IRF530 | TO220BV | Q1_N
2 | IRF9530 | IRF9530 | TO220BV | Q2_P
2 | JUMPER-SMT_2_NC_PASTE_SILK | JUMPER-SMT_2_NC_PASTE_SILK | SMT-JUMPER_2_NC_PASTE_SILK | JP1
1 | L293D | L293D | DIL16 | IC1 | PUSH-PULL 4 CHANNEL DRIVER |  |  |  |  |  |  |  |  |  | L293D | 9589619 | 56P8249 | 16
1 | LED_RED_0805 | LED_RED_0805 | RED_LED | PWR
1 | M02_RMC | M02_RMC | M02_RMC | SUPPLY_OUT
1 | MINI-USB-32005-201 | MINI-USB-32005-201 | 32005-201 | USB | MINI USB-B Conector |  |  |  |  |  |  |  |  |  |  | unknown | unknown | 5
1 | MOMENTARY-SWITCH-SPST-PTH-RIGHT-ANGLE-KIT | MOMENTARY-SWITCH-SPST-PTH-RIGHT-ANGLE-KIT | TACTILE_SWITCH_PTH_RIGHT_ANGLE_KIT | RESET | Momentary Switch (Pushbutton) - SPST |  |  |  |  |  |  |  |  |  |  |  |  |  | CONN-10672 | COM-10791
2 | SCREW_TERMINAL_5.08 | SCREW_TERMINAL_5.08 | SCREW_TERMINAL_5.08 | #ERROR!
1 | SI2302 | SI2302 | SOT95P240X110-3N | U1
1 | STM32F103C8T6 | STM32F103C8T6 | QFP50P900X900X160-48N | IC2 | Mainstream Performance line
2 | WIREPAD4

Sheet: BOM_DisplayBoard
Part | Value | Device | Package | Description | POPULARITY | SPICEPREFIX
DOWN | PUSH_SWITCH_MOM | PUSH_SWITCH_MOM | HDRRAR4W64P254_2X2_1016X736X556B
J4 |  | CONN_16 | 1X16 | Multi connection point. Often used as Generic Header-pin footprint for 0.1 inch spaced/style header connections
LCD | 2.4_INCH_LCD_ILI9341 | 2.4_INCH_LCD_ILI9341 | XTAL1150X490X450N
LEFT | PUSH_SWITCH_MOM | PUSH_SWITCH_MOM | HDRRAR4W64P254_2X2_1016X736X556B
MENU | PUSH_SWITCH_MOM | PUSH_SWITCH_MOM | HDRRAR4W64P254_2X2_1016X736X556B
MID | PUSH_SWITCH_MOM | PUSH_SWITCH_MOM | HDRRAR4W64P254_2X2_1016X736X556B
PWR | LED_RED_0805 | LED3MM | LED3MM | LED | 97
R1 | 1K | R-US_R0805 | R0805 | RESISTOR
R2 | 1K | R-US_R0805 | R0805 | RESISTOR
RIGHT | PUSH_SWITCH_MOM | PUSH_SWITCH_MOM | HDRRAR4W64P254_2X2_1016X736X556B
START | PUSH_SWITCH_MOM | PUSH_SWITCH_MOM | HDRRAR4W64P254_2X2_1016X736X556B
STATUS |  | LED3MM | LED3MM | LED | 97
SUPPLY_IN | M02_RMC | M02_RMC | M02_RMC
UP | PUSH_SWITCH_MOM | PUSH_SWITCH_MOM | HDRRAR4W64P254_2X2_1016X736X556B

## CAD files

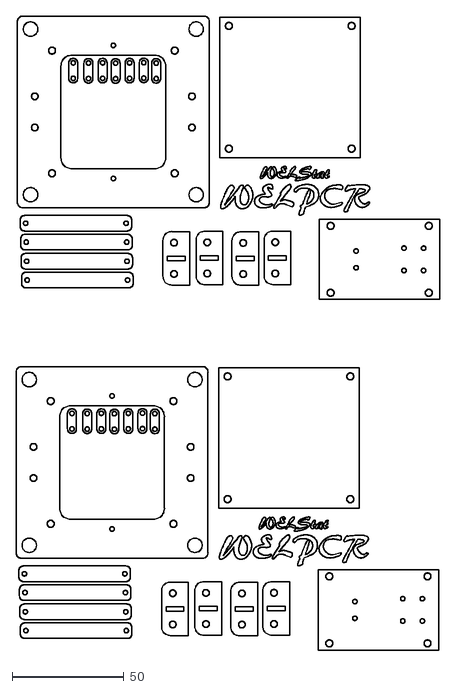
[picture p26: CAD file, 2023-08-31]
Mechanical_design_files/Laser cutting for 2 PCR.dxf
190.0 x 284.2

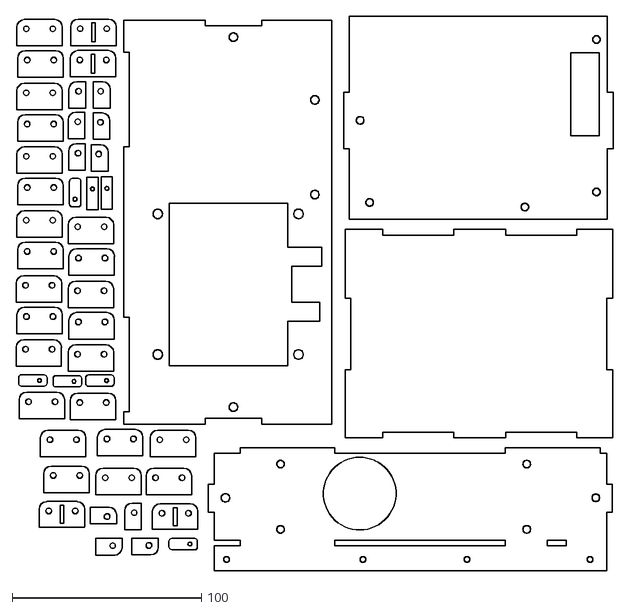
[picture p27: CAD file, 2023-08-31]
Mechanical_design_files/PCR Casing/Body/PCR casing modified sheet 2.dxf
315.3 x 292.7

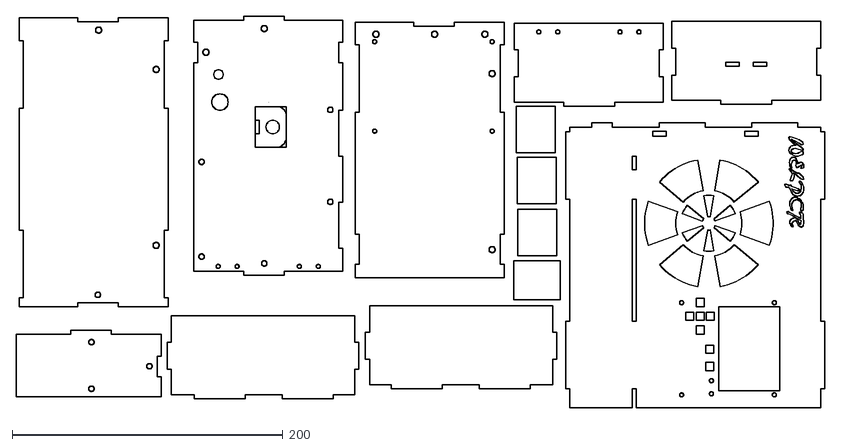
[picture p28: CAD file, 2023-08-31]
Mechanical_design_files/PCR Casing/Body/PCR casing modified sheet 1.dxf
597.1 x 289.1

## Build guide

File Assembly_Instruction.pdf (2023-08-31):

## WELPCR Mechanical Assembly Instructions

- Step1: Make the BOM for WEL PCR and place the order. Here is the WEL_PCR_BOM. (https://docs.google.com/spreadsheets/d/14mXDqKmedVw8rvZARGVxLZBP766ubliR-aTVFx6Z4ps/edit)
- Step2: For mechanical design, we need these following design files.
- WEL_PCR Motherboard
- WEL-PCR Display Board
- Metal laser cutting Design
- For metal laser cutting, we went to
Falcon Engineering & Laser Services,CNC (https://goo.gl/maps/vn7VjcVYdo3mLXKL8?coh=178571&entry=tt) files from Machine Tool Lab,IIT Bombay. (https://goo.gl/maps/NwYoFveUBiqyFyHM9?coh=178571&entry=tt)
- CNC design files from machine and tool lab, IIT Bombay For Lid and Tube holder, we need aluminium block of the following dimension
For 1-piece LID: 3-inch x 3-inch x 1 inch
For tube holder (9): 2.5-inch x 2.5-inch x 1 inch
- WELPCR casing laser cutting on acrylic sheet from ELL, IIT Bombay.
- Step3: Solder all the components to printed circuit boards (both Motherboard and the display board following the Schematic file and BOM).
- Display board

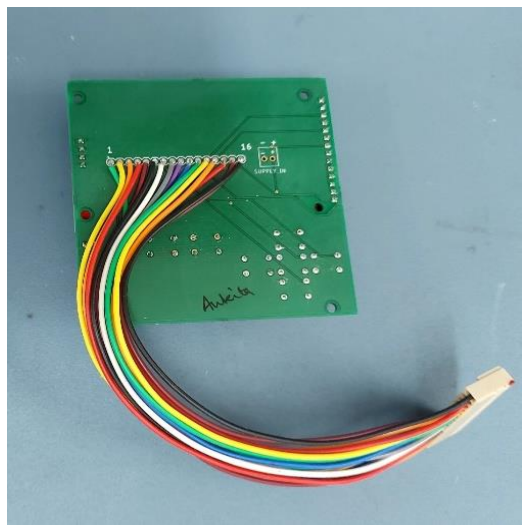
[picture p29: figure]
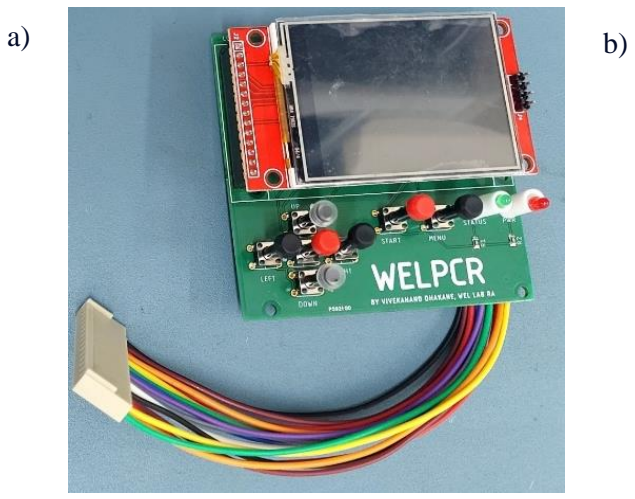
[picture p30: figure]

Figure 1:(a) Front view and (b) Back view of the display board

- Motherboard
- Frontside: Do not forget to add a reg of value 5-10 kΩ in U1 and a Zener diode of 3.3V in reverse bias on the regulator (REG) as mentioned in the figure 2(a).These are implemented to protect the controller. Make sure to thicken the paths connecting the H-Bridge.
BLOCK_TEMP and LID_TEMP misprinted somehow. We marked an arrow to show the correct variable name on the PCB.
- Backside: One TVS diode of 12V between positive and negative terminal of power supply.

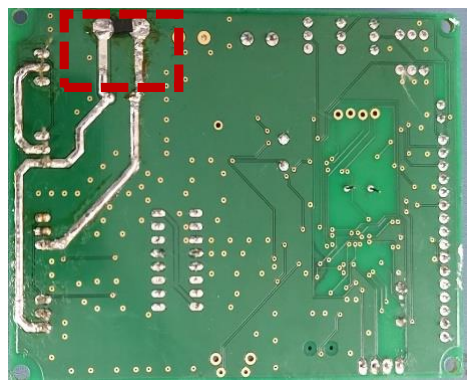
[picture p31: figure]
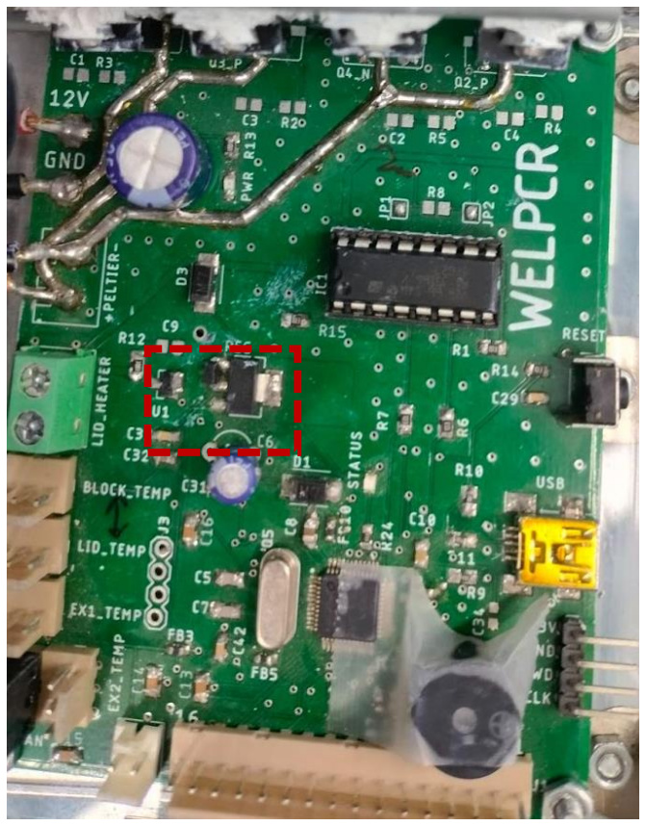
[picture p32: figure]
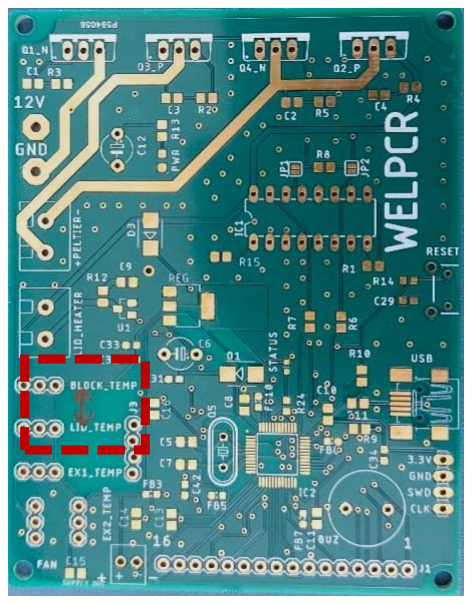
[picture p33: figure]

Figure 2: (a) Motherboard highlighting U1 and REG (b) 12V TVS diode

(c) Interchanging of BLOCK_TEMP →LID_TEMP

a)
b)

c)

Mechanical Assembly

- Heater lid and Tube holder

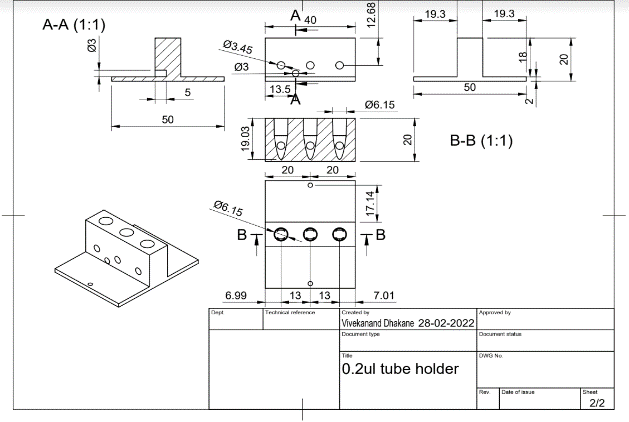
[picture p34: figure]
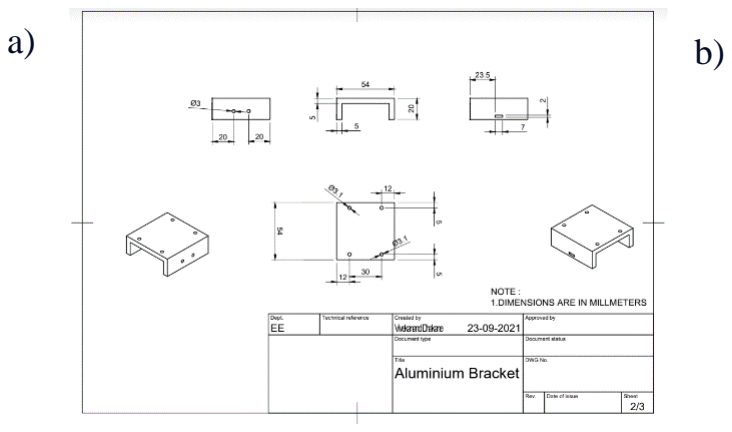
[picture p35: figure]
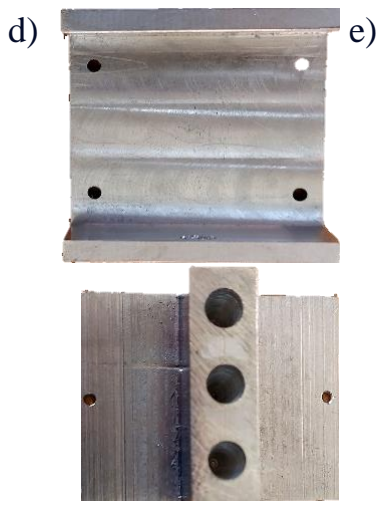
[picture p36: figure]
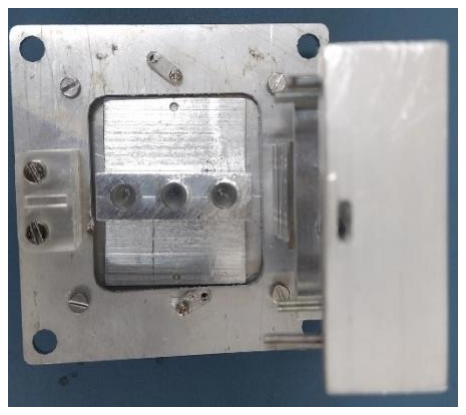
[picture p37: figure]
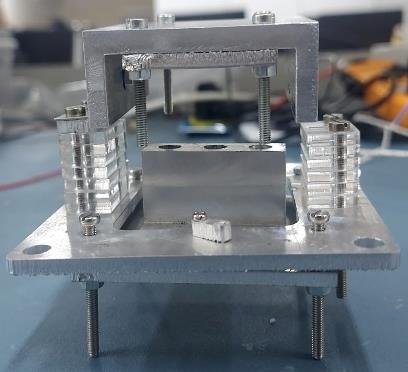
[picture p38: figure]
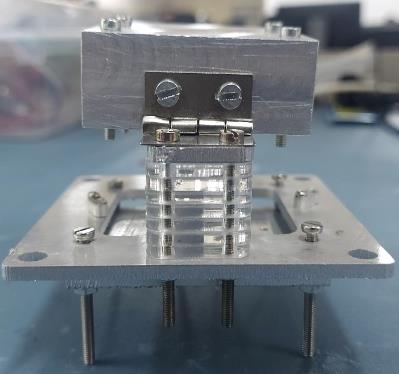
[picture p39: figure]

Attach a hinge between the metal lid and the metal plate and connect with the acrylic “C” shaped laser cutting to adjust the height of the tube holder.

c)

f) | g) | h)

Figure 3: (a) Design of the heater lid (b) Design of tube holder (c) Milling machine at Machine and tool lab, IIT Bombay (d) Heater lid and tube holder made from aluminium block (e) Top view of the lid assembly while lid is closed (f)Front view of the tube holder and lid assembly (g)Left side view, hinge joint (h) Top view of the lid assembly while lid is open

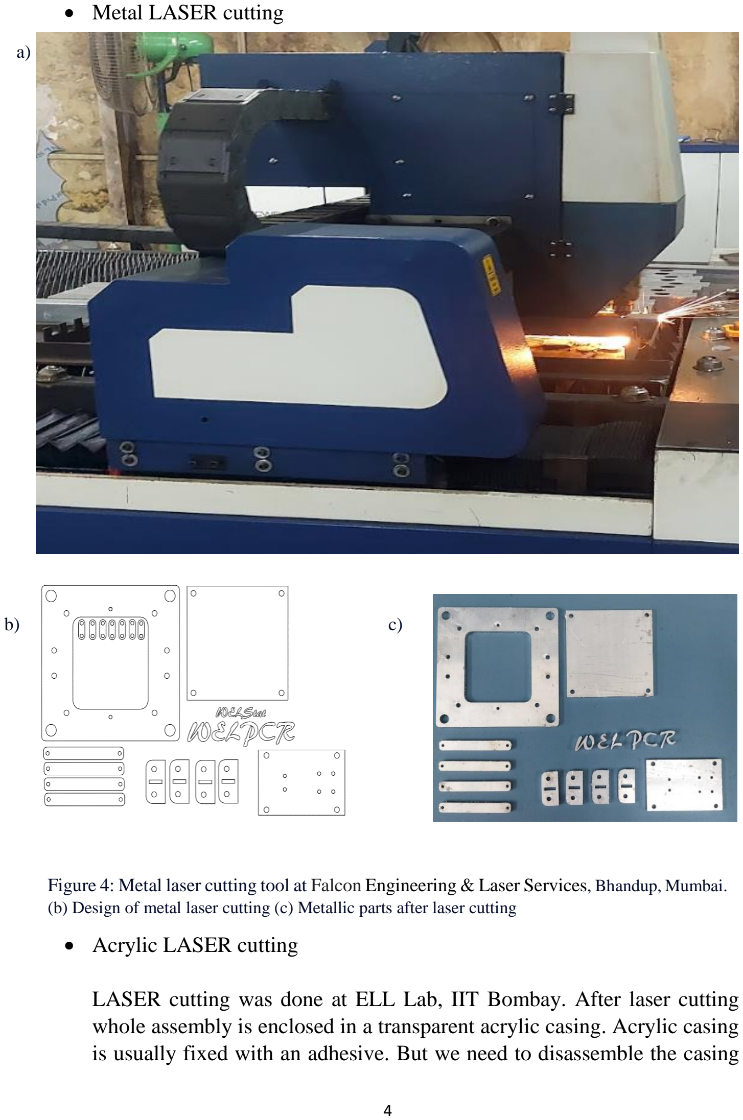
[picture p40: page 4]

- Metal LASER cutting
- Acrylic LASER cutting

LASER cutting was done at ELL Lab, IIT Bombay. After laser cutting whole assembly is enclosed in a transparent acrylic casing. Acrylic casing is usually fixed with an adhesive. But we need to disassemble the casing

a)

b) c)

Figure 4: Metal laser cutting tool at Falcon Engineering & Laser Services, Bhandup, Mumbai.
(b) Design of metal laser cutting (c) Metallic parts after laser cutting many times. So, we use the L-bracket with nut-bolt to connect two right angular faces. For maintenance we may need to open one face of the casing. For that, front face is fixed using a hinged on one side. Front of the WELPCR can be opened easily for maintenance purpose.

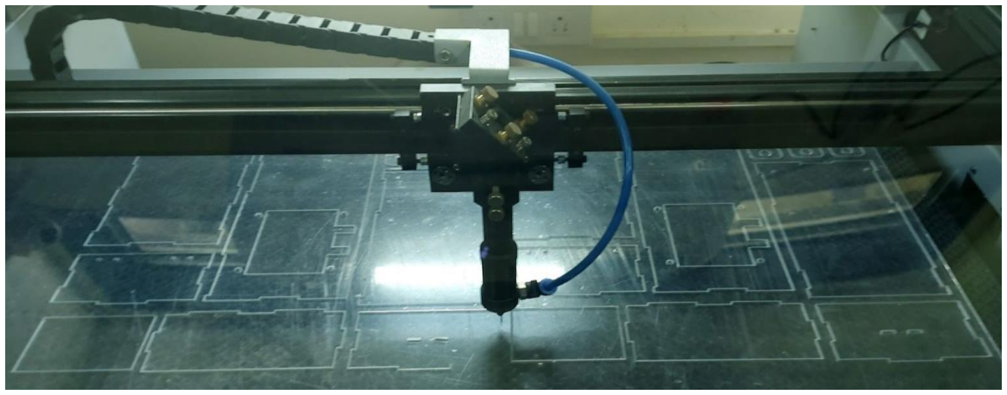
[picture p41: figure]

- Lid Heater

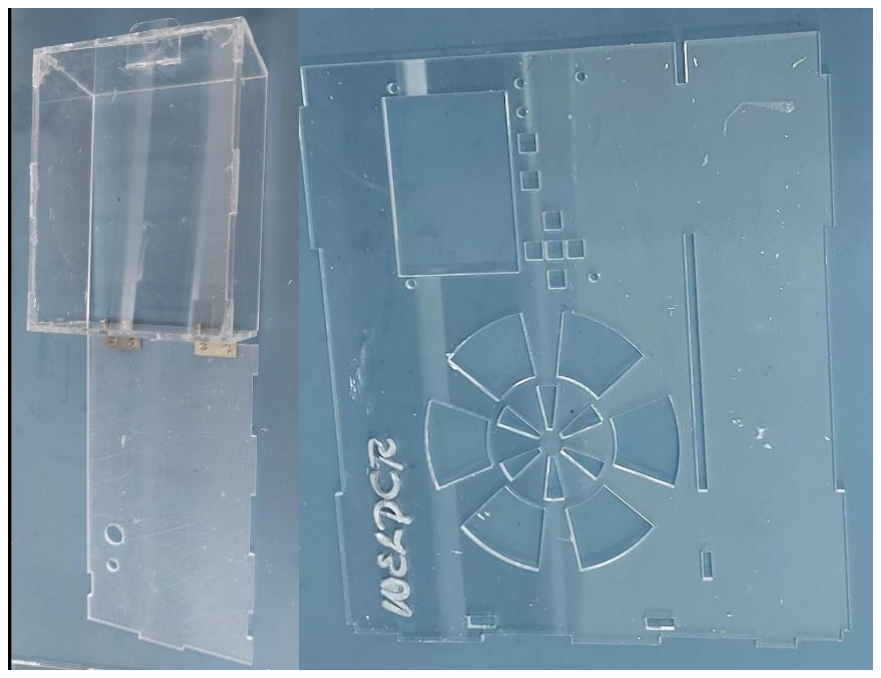
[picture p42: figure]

We have used nichrome wire and mica sheet to assemble the lid heater. Two terminals of the nichrome wires are connected to the Vdd and ground pin of the LID_HEATER point on the motherboard. Add thermal paste and assemble with a copper wire.

a)

Figure 5: (a) LASER cutting at ELL, IIT Bombay (b) Casing assembly after the LASER cutting

b)

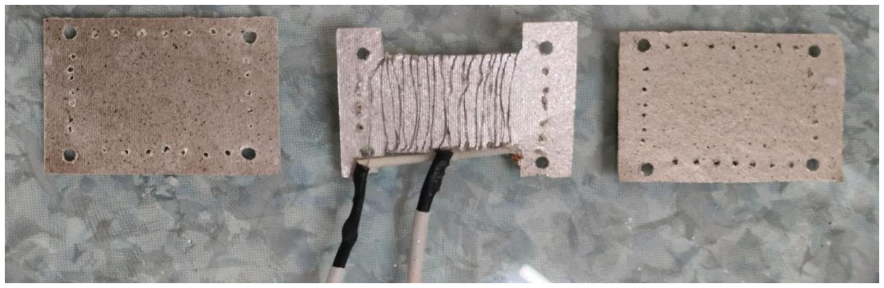
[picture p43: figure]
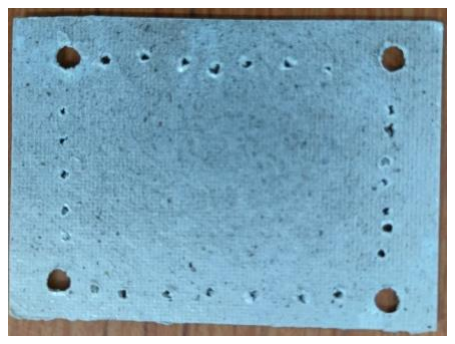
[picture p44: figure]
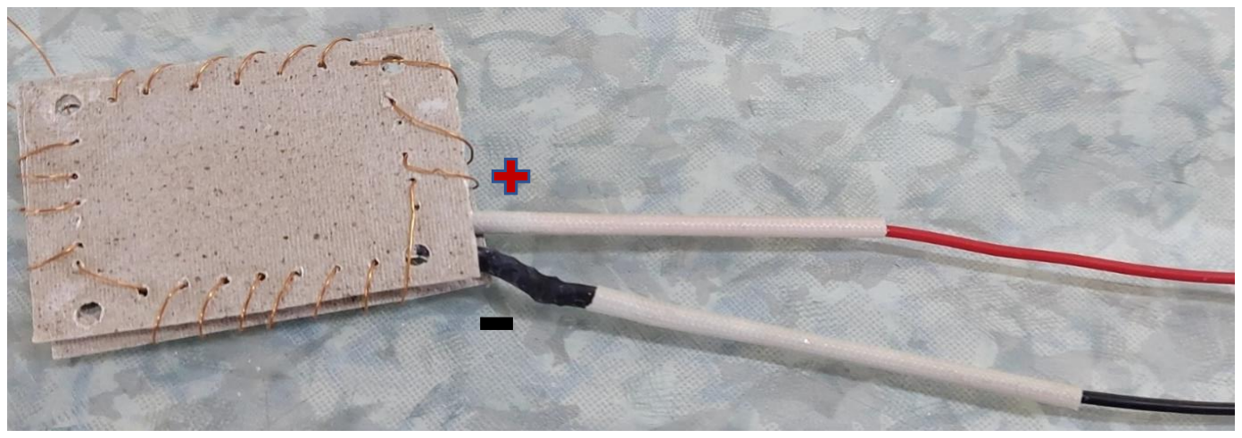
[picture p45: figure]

- Assembly Instructions

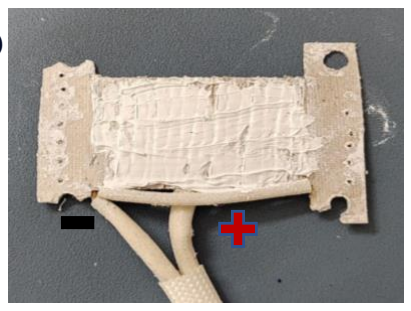
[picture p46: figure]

1. Cut out 3 rectangles out of mica sheets of dimension (5.4 X 3.6 cm).
2. Cut out a H-shape out of a rectangle and wrap nichrome wire around it, leaving out 3 terminals (2 on the ends and 1 in the middle).
3. Drill four holes of diameter 3mm onto four corners of the mica sheet aligning with the covering metal sheet’s holes.
4. Connect the ground terminals together with a copper wire protected from an insulation tube to avoid shorting of the circuit.

a)

b) | c) | d)

e)

Figure 6: (a) 3 rectangular mica sheets (b) After drilling the holes (c) Added thermal paste
(d) Nichrome wire assembly along with thermal paste (e) Live wire connection to the nichrome heater.

5. Connect the ground and live terminal with black and red multi thread wires and securing them through a heat slue and then insulation tubes.
6. Apply thermal paste on the nichrome coil for ensuring even spread of heat once in work.
7. Needled holes on periphery of the mica sheet rectangles and coil them together with copper wire.
8. Secure both the live and ground wires in an insulation tube.
9. Connect the live and ground wires to the LID_HEATER point on the motherboard.
- Thermistor
1. Take two, 2 mm thermistor and add the two terminals with live(red) and output wires(brown) of a 3 Pin RMC female connector each. Ground line (black) and the output (brown)will be sorted by one 1 kΩ through hole resistor.
2. Secure both the live and output wires with an insulation tube as shown in the figure 7.
- Peltier

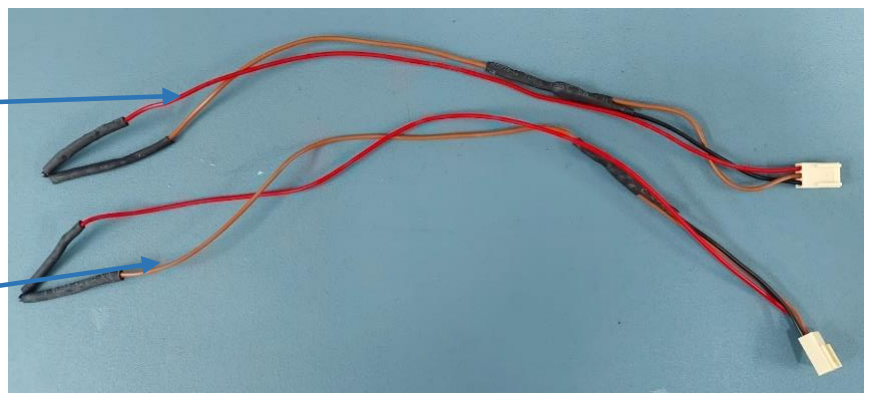
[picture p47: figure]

Figure 7: Thermistor assembly with 3 Pin RMC female connector

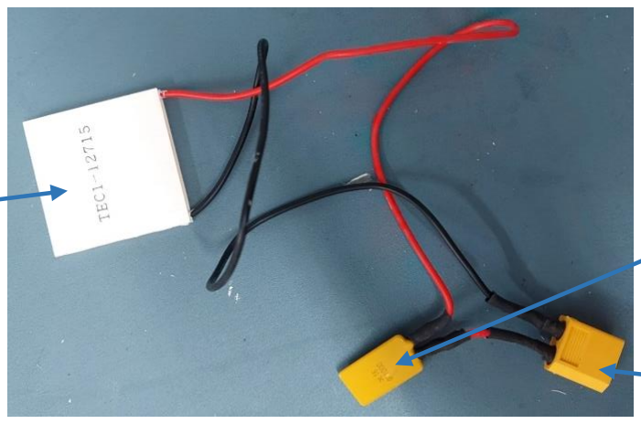
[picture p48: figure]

Figure 8: Peltier heat sink assembly

15A fuse

XT60 Male
Connector

10A Peltier

Live wire

Output wire

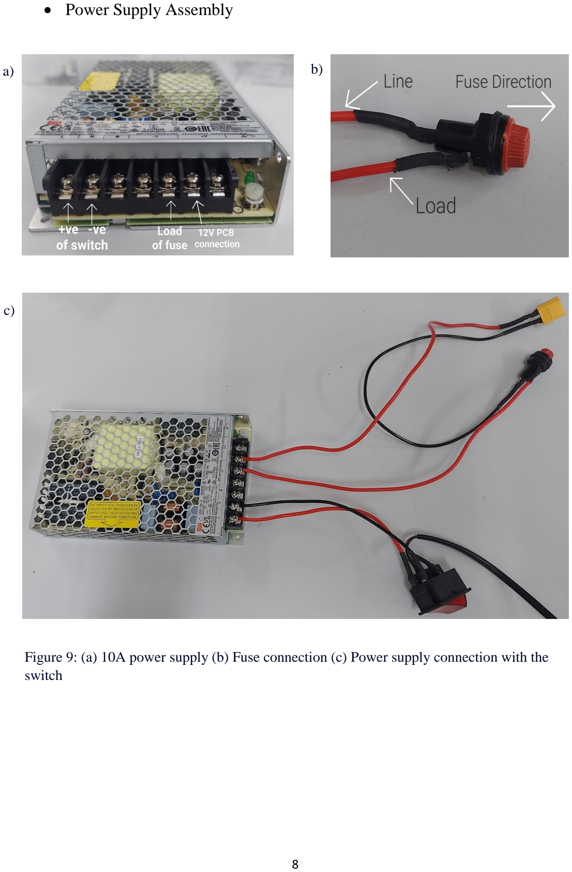
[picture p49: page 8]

- Power Supply Assembly
a) b)

c)

Figure 9: (a) 10A power supply (b) Fuse connection (c) Power supply connection with the switch

- Cooling Fan assembly

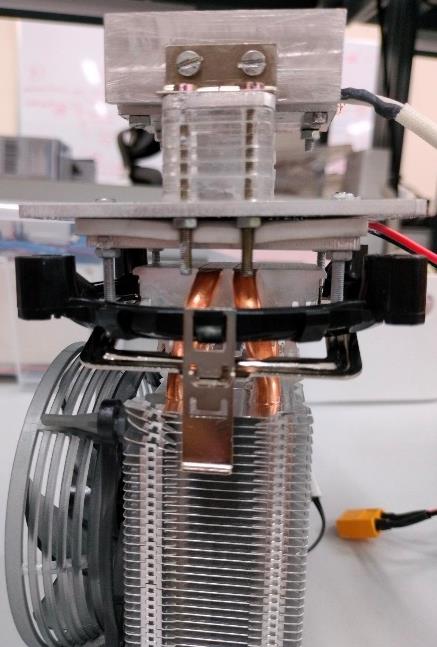
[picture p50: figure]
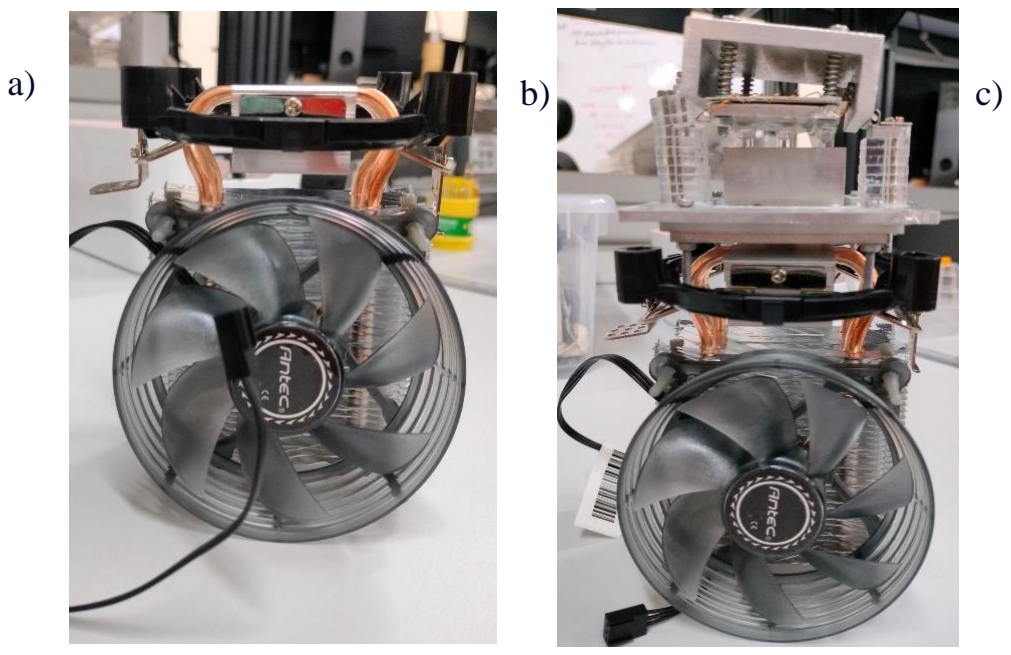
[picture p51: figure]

Figure 10: (a) Cooling fan (b) Fan connection with the tube holder, lid and peltier assembly (front view) (c) Fan connection with the tube holder, lid and peltier assembly (side view)

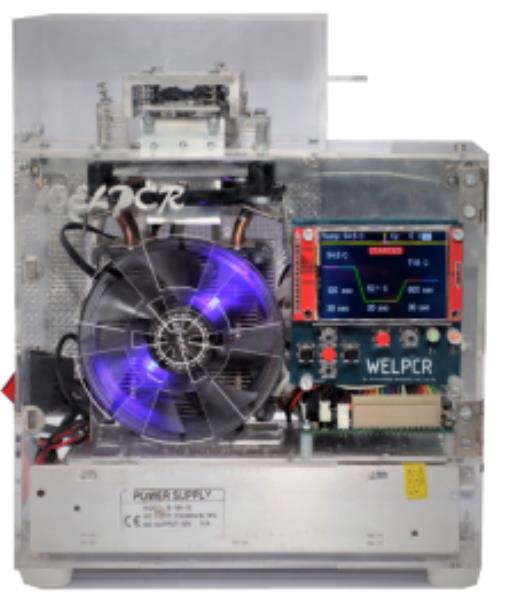
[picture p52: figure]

Figure 11: Fully assembled WELPCR

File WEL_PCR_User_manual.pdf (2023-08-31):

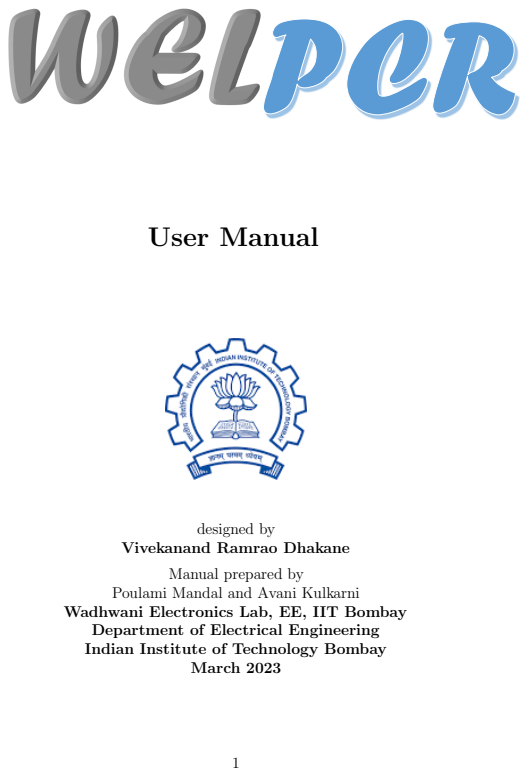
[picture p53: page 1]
User Manual; designed by; March 2023

Vivekanand Ramrao Dhakane

Manual prepared by

Poulami Mandal and Avani Kulkarni

Wadhwani Electronics Lab, EE, IIT Bombay
Department of Electrical Engineering
Indian Institute of Technology Bombay

## Contents

1 Introduction to WEL-PCR | 3
2 Operating Procedure | 9
3 Maintenance | 10

## 1 Introduction to WEL-PCR

WELPCR is a PCR (Polymerase Chain Reaction) machine made by taking OpenPCR as a reference. The main improvement made in WELPCR with respect to OpenPCR is that WELPCR is a standalone device and does not require external device like computer or mobile to configure it.

### 1.1 System Overview

The PCR base includes:

- Reaction Module Bay - It holds the inserted reaction module
- Reaction module locking bar-It locks the inserted module in place
- Control Panel- It provides access to all the functions needed to create and run PCR protocols .
- Air vents-Air Vents allow the thermal cycler to heat and cool quickly .

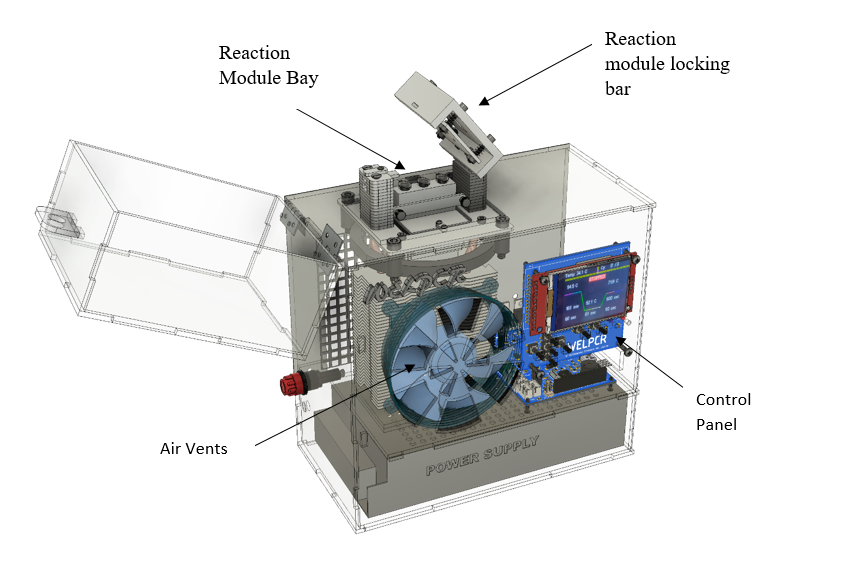
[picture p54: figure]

Figure 1: Front view of the WEL-PCR

- Liquid crystal display(LCD)-It displays the main menu and the other screens.

- Command and navigation keys-We can use these keys to set the desired reaction parameters and to navigate various screens.
- Tube holder-The tube holder is the main part of this PCR which can hold 3 microcentrifuge tubes into this block. This block is heated by Peltier.
- Peltier-A Peltier is a heat pump that can pump heat from one side to the other side depending on the direction of the current flow. We can heat and cool the same side just by inverting the supply connections. So both rising and lowering the temperature can be controlled precisely.
- Lid heater-Lid heater is a ceramic 12v 40W ceramic cartridge heater, commonly used in 3d printers .

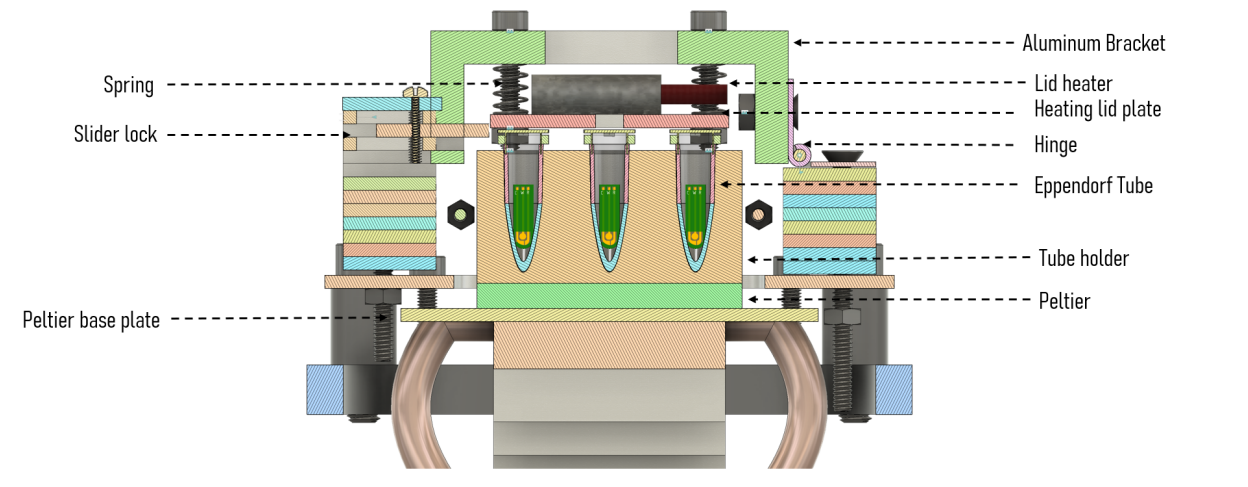
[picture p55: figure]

Figure 2: Crosssection view of the WEL-PCR

- Heating lid plate-The heating lid plate is heated by a lid heater. This plate is used to heat the lids of tubes to avoid condensation of liquid sample vapor underneath the tube cap.
- Aluminium Bracket-:It is a solid square bracket ‘[’ shaped lid. This is the lid that presses the heating lid plate on the lids of the tube. Tension on the heating lid is maintained due to the spring between the bracket and the heating plate.
- CPU cooler-There is no CPU in this PCR machine, but this big heat sink with a cooling fan is a part of the desktop CPU used for cooling the microprocessor. This CPU cooler is used to sink(while decreasing the temperature) and source(while increasing the temperature) the heat.
- Peltier base plate- Peltier base plate is used as an interface between the CPU cooler and the Peltier. The shape and area of the Peltier and the CPU cooler are not the same ,so to collect heat from the whole area of the Peltier and to pass that heat to the CPU cooler, this Peltier base plate is used.
- Microcentrifuge tubes-These are tubes made for preparing, mixing, centrifuging, storing, and transporting solid and liquid reagents and samples. We use 0.2ml eppendorf tubes.

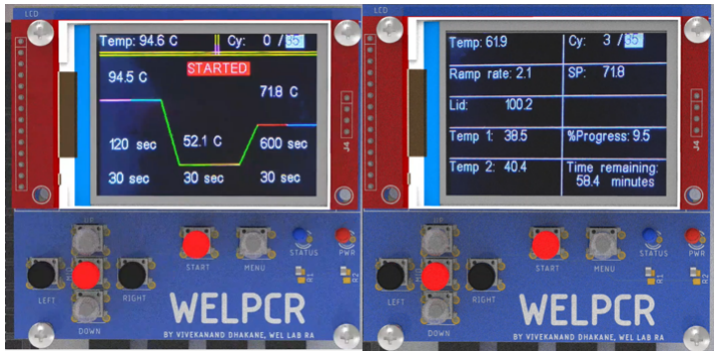
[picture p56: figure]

Figure 3: Components of the control panel on WEL-PCR

The main screen is displayed after the power is on. Figure 3 shows the components of the control panel. WELPCR has a 2.4′′ touch screen 240x320 display.The display has two windows. The first window is the ‘PCR Parameter Window,’ and the second window is the ‘PCR Parameter Monitor Window’. In the PCR parameter window, we can see the current parameters of the single PCR cycle, which are temperature and time for denaturation, annealing, and extension. These parameters can be selected and changed by the navigation keys. The second window, the ’PCR Parameter Monitor Window’, is for monitoring the live parameters.

PCR parameter window:

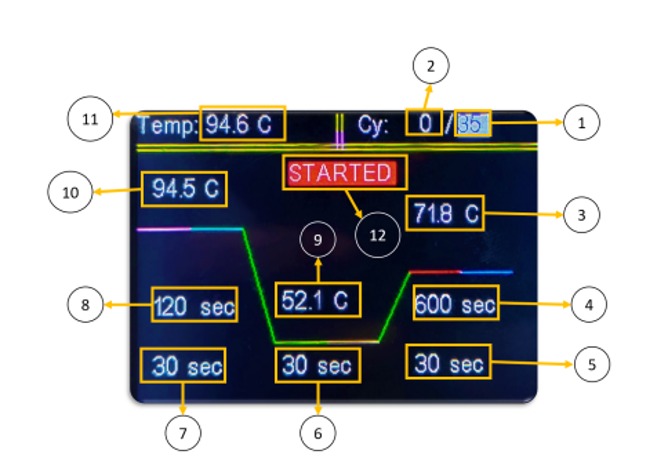
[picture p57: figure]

Figure 4: Details about the PCR parameter window

1. The total number of cycles
2. The number of cycles completed
3. Extension temperature
4. Extension time for the last cycle
5. Extension time of a single cycle
6. Annealing time
7. Denaturation time
8. Initial denaturation temperature
9. Annealing temperature
10. Denaturation temperature
11. The current temperature of the tube holder
12. ‘STARTED’ or ‘STOPPED’ indicates the current state of PCR.

PCR parameter monitor window:

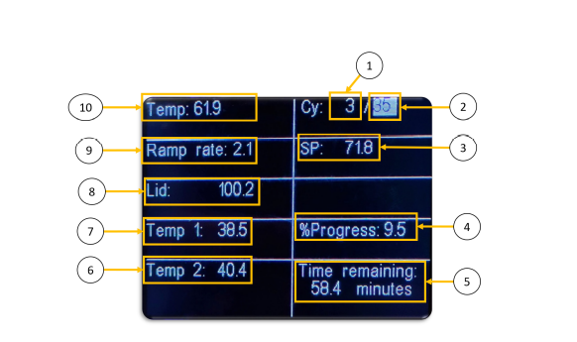
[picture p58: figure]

Figure 5: Details about the PCR parameter window

1. The number of cycles completed
2. The total number of cycles
3. The current set point of the PID controller
4. Percentage progress of the current PCR test
5. Time remaining for the current PCR test
6. Temperature measured by the temperature sensor probe
7. Temperature measured by the temperature sensor probe 2
8. Temperature of the heated lid
9. Current Ramp rate
10. Current tube holder temperature

PCR front panel:

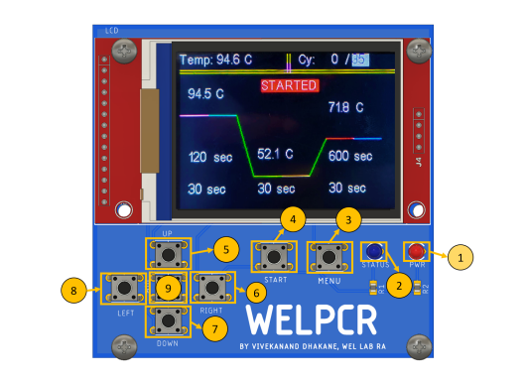
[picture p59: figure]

Figure 6: Front panel of WELPCR

1. Power LED
2. Status LED
3. MENU: To change the window
4. START: Long press to start or stop the test
5. UP: Shift the cursor up
6. RIGHT: Shift the cursor right
7. Down: Shift the cursor down
8. LEFT: Shift the cursor left
9. MID: Select the parameters

## 2 Operating Procedure

1. Set up the PCR reaction as per the protocol. Apply thermal paste to the tube walls and insert the tubes in the tube holder. Carefully lock the lid ensuring no gap between the tube and the lid to avoid condensation.
2. On PCR Parameter Window, navigate using the navigation keys. Select the parameters to be changed using the MID button, the parameter gets highlighted in green, and adjust them using the navigation keys. Once the value is set for a particular parameter again press the MID button. Repeat similar steps until all the values are set as per the reaction conditions. UP and DOWN keys change the parameter by 0.1 if it is temperature and change it by 1 if it is time and cycle. LEFT and RIGHT buttons change the parameters by 10.
3. Once the parameters are set, long-press the START button to start the test. The status on the screen will be changed to STARTED. Change the window using the MENU button to see real-time parameters like remaining time and percentage progress.
4. Once the test is completed, the status on the screen will be changed to STOPPED.

## 3 Maintenance

### 3.1 Cleaning

The WEL-PCR requires little maintenance for proper operation and precise thermal control. However,with long and constant use,the thermal cycler requires some cleaning and maintenance .
Do’s
1. The WEL-PCR should be cleaned with a soft cloth on a regular basis and occasionally use IPA to remove any debris or dirt that might interfere with proper functioning.
2. To prevent electrical shock,always turn off and unplug the instrument before cleaning it.

Dont’s

1. Do not use abrasive detergents or rough material since they scratch the control panel.
2. Never use cleaning solutions that are corrosive to aluminium. Avoid scratching the surface of the bay which interfaces with precise thermal control.
3. Never pour water or other solutions in the reaction module bay. Wet components can cause electrical shock when the thermal cycler is plugged in.

### 3.2 Important Instructions

1. If the WEL-PCR does not turn on, first check that the power cord is plugged into a functioning power source. Also, check that the power cord and power source are within the specifications of this instrument.

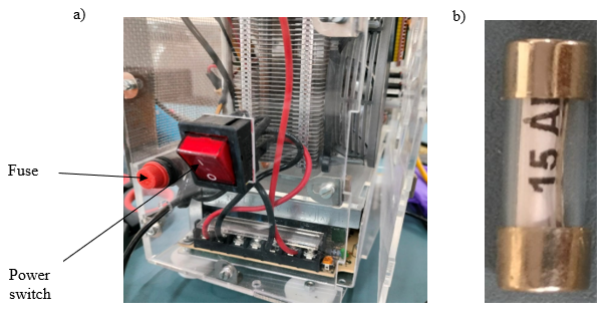
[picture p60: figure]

Figure 7: Details of the fuse a) Position of the fuse b) 15A fuse

2. To prevent electrical shock, always turn off and unplug the instrument from an electrical outlet before checking the fuses. If the fuse is damaged, replace it with the correct fuse and close the knob. A bad fuse shows a broken or burned spot in the metal; a good fuse has intact metal.

In case of any problem or queries kindly contact us.

Contact details
Mr.Mahesh Bhaganagare
Sr Technical Superintendent
WEL, Electrical Engineering Department Indian Institute of Technology Bombay mab@ee.iitb.ac.in
Contact Number- 022 2576 3524

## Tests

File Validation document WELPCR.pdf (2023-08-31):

Validation protocol for WELPCR

Aim: To validate WELPCR

Objectives:

To isolate and quantify RNA

To synthesize cDNA, quantify and prepare 10-fold serial dilutions (107-102

copies)

To amplify cDNA and make endpoint analysis comparing WELPCR and

commercial thermal cycler

To determine DNA concentration real-time by optical detection using Methylene

Blue (MB) and compare with fluorescent detection using SYBR Green kit.

Protocols

1. Equipment specifications: Thermal cyclers—Electrophoresis equipment
2. Samples and sample preparation: Strain of interest—DNA extraction and purity

checking—Different concentrations prepared by serial dilution of stock DNA

3. Amplification mix: Concentration—Recommended protocol
4. Primers: Concentration—Sequence (FP/RP)—Annealing temperature—

Extension time

5. Amplification protocol: Identical PCR program and conditions for thermal

cyclers under study

6. Documentation of PCR products: Visualization of PCR products by 1% AGE
7. Quantification: Total amount and purity of the amplified product can be

determined by UV Spectrophotometer (using purified PCR product)

8. Determination of detection threshold at the lowest concentration of template

DNA (Sensitivity)

9. Robustness: Validate reproducibility by same DNA concentration and target on

thermal cyclers—AGE—Gel purification/ UV Spectrophotometer.

Reference:

González-González, E., Mendoza-Ramos, J. L., Pedroza, S. C., Cuellar-

Monterrubio, A. A., Márquez-Ipiña, A. R., Lira-Serhan, D., ... & Alvarez, M. M.

(2019). Validation of use of the miniPCR thermocycler for Ebola and Zika virus

detection. PLoS One, 14(5), e0215642.

Park, C. Y., Kim, J. D., Kim, Y. S., Song, H. J., Kim, J. M., & Kim, J. (2012). Cost

reduction of PCR thermal cycler. International Journal of Multimedia and

Ubiquitous Engineering, 7(2), 389-394.

10.Real-time detection:

a. Optical detection: Using 50μM Methylene blue (MB) and different DNA

concentrations.

b. Fluorescence detection: Using SYBR green dye for comparing EC results.
c. Determine PCR efficiency and determine detection limit.

Reference:

Tseng, H. Y., Adamik, V., Parsons, J., Lan, S. S., Malfesi, S., Lum, J., ... & Gray,

B. (2014). Development of an electrochemical biosensor array for quantitative

polymerase chain reaction utilizing three-metal printed circuit board technology.

Sensors and Actuators B: Chemical, 204, 459-466

Wang, K., Chen, Y. P., Lei, Y., Zhong, G. X., Liu, A. L., Zheng, Y. J., ... & Chen,
Y. Z. (2013). Electrochemical method for monitoring the progress of polymerase chain reactions using Methylene blue as an indicator. Microchimica Acta, 180(9), 871-878.

Won, B. Y., Shin, S., Baek, S., Jung, Y. L., Li, T., Shin, S. C., ... & Park, H. G. (2011). Investigation of the signaling mechanism and verification of the performance of an electrochemical real-time PCR system based on the interaction of methylene blue with DNA. Analyst, 136(8), 1573-1579.

Strain: Bacteriophage phi 6

1. Isolation of RNA from free viral particles

Kit: GenElute™ Total RNA Purification Kit

1.1. Protocol:

### 1. Preparation of lysate:

a. Transfer up to 100μL of viral suspension to an RNase-free microcentrifuge

tube.

b. Add 350μL of Buffer RL. Vortex for 15secs in order to lyse the viral cells.
c. To this add 200μL of 96–100% ethanol. Mix by vortexing for 10secs.

### 2. Binding RNA to column:

a. Assemble the column with collection tube.
b. Add 600μL of lysate to the column and centrifuge for 1 minute at ≥3,500 × g

(~6,000 rpm).

c. Ensure the entire lysate volume has been transferred. If required spin for an

additional 1 minute at 14,000 × g (~14,000 rpm).

d. Discard the flowthrough and reassemble the spin column with its collection

tube.

e. Repeat the above steps depending on the lysate volume.

### 3. Column wash:

a. Add 400μL of Wash Solution A to the column and centrifuge for 1 minute at

≥3,500 × g (~6,000 rpm).

b. Inspect the column to ensure the entire solution has passed through. If

necessary, give an additional spin for 1 minute at 14,000 × g (~14,000 rpm).

c. Discard the flowthrough and reassemble the spin column with its collection

tube.

d. Repeat above column wash steps for additional two times.
e. After final wash spin the column for 2 minutes to dry the resin completely.
f. Discard the collection tube.

### 4. RNA elution:

a. Place the column in a 1.7ml elution tube.
b. Add 50μL of Elution Solution A to the column.
c. Centrifuge for 2 minutes at 200 × g (~2,000 rpm), followed by 1 minute at

14,000 × g (~14,000 rpm).

d. Note the volume eluted from the column. If the entire 50μL has not been

eluted spin the column for an additional 1 minute at 14,000 × g (~14,000

rpm).

e. For maximum RNA recovery, it is recommended that a second elution be

performed into a separate microcentrifuge tube (Repeat the above steps).

### 5. Storage of RNA:

a. Purified RNA samples may be stored at -20 °C. For long term storage

samples may be placed at -70 °C

### 2. RNA qualitative and quantitative analysis

RNA Quantification (Thermo Scientific Multiskan GO)

A ratio of 2.0 from A260:A280 indicates pure RNA.

### 2.1. Protocol

a. Select ‘DNA/RNA’ option under the cuvette tab on the home screen.
b. Select RNA from the menu.
c. Pathlength correction: Yes. Pathlength: 10mm
d. Clean the cuvette with 50μL of Milli Q water twice.

e. Set blank by using 50μL of MilliQ. Press the F2 key for Zeroing the

instrument.

f. Clean the cuvette and add 49μL of Milli Q and 1μL of RNA sample to be

quantified.

g. Insert the cuvette into the port and press the Start/On key to initiate the

measurement.

h. Take each reading twice and note down the values.
i. After each reading clean the cuvette with Milli Q thoroughly.
j. When using different cuvettes, the blank has to be set up for each tube.

### 3. cDNA synthesis

Kit: iScript cDNA synthesis kit

Components | Volume per reaction (μl)
5x iScript Reaction Mix | 4
iScript Reverse Transcriptase | 1
Nuclease Free Water | 14
RNA template (100fg-1μg)* | 1
Total volume | 20
*When using large amount of input RNA(>1μg), the reaction should be scaled up. Example: 40μl reaction for 2μg, 100μl reaction for 5μg.

Reaction Protocol:

Steps | Temperature | Time (minutes)
Priming | 25°C | 5
Reverse transcription | 46°C | 20
RT inactivation | 95°C | 1
Optional step | 4°C

### 4. Polymerase Chain Reaction

4.1. Reagents:

a. Primers: Sigma (503bp)
Oligo Name | Sequence
503bp Forward | 5'-GAACCATATGACTTTGTACCTGGTCC-3'
503bp Reverse | 5'-CAACGAATTCTCAGGCGCTTACCTCATC-3'
b. Master Mix: PCR Master Mix 2X (Cat. No. K0171) Thermo scientific
c. Nuclease Free Water
d. Template (cDNA)
e. Reaction volume: 20μL
3.2. Preparation of master mix:
a. In a sterile vial, add nuclease free water followed by Master Mix (2X).
b. Add forward and reverse primers and mix well.
c. Aliquot 19μL of master mix into each sterile PCR vials.

Table 3: PCR reaction mixture

Reagents | Volume per reaction
Template (cDNA) | 1μL
Forward Primer | 1μL
Reverse Primer | 1μL
Master Mix (2X) | 10μL
NFW | 7μL
Total Volume | 20μL

d. Add 1μL of isolated DNA to the master mix and ensure proper mixing of the

contents.

e. Place the PCR tubes in thermal cycler with the program set to appropriate

temperature and time.

f. After the PCR run is complete, PCR products can be visualized by Agarose

Gel Electrophoresis or can be stored for further analysis.

*Annealing temperature depends upon primers

**Extension time will depend upon amplicon length

### 5. Quantification of amplified product

5.1. Agarose gel electrophoresis
1. Preparation of gel:
a. Gel tray was placed in casting apparatus and the combs were inserted into

the place.

b. For preparation of 1% agarose gel, 0.5gm of agarose was weighed and

dissolved in 50mL of 1X TBE buffer (Stock 5X).

c. The mixture was heated to dissolve agarose in the solution. Swirl the flask

intermittently to check if agarose is dissolved completely.

Table 4: PCR thermal cycling conditions

Steps | No. of cycles | Temperature | Time
Initial Denaturation | 1 | 95°C | 120 sec
Denaturation | 35 cycles | 95°C | 30sec
Annealing | | 52.8°C | 30 sec
Extension | | 72°C | 30sec
Final Extension | 1 | 72°C | 600 sec

d. Add 2μL of EtBr after cooling the gel for a few minutes.
e. The mixture was then poured into the prepared casting tray ensuring no air

bubbles and allowed to set.

2. Preparation of tank buffer:
a. 5X TBE was diluted to 1X and 250mL (300mL) was used as tank buffer.
3. After the solidification of gel, the gel tray was placed inside the tank

buffer and then the combs were removed.

4. 2μL of DNA sample (PCR product) was mixed with 1μL of loading dye

and 7μL 1X TBE buffer and loaded into each well.

5. 0.5μL of DNA ladder mixed with 1μL of 10X FastDigest Green Buffer

and 8.5μL of 1X TBE was added.

6. Voltage of 100V was applied and electrophoresis was allowed to run for

45minutes.

7. The gel was then visualised under a UV transilluminator.

### 5.2. Notes:

1. Loading dye: FastDigest Green Buffer (10X) Thermo Scientific
2. DNA Ladder: GeneRuler 1 kb DNA Ladder (Thermo Scientific)
3. Use a separate glove while handling the flask and EtBr vials to avoid direct

contact with EtBr.

4. For eluting DNA from the gel (gel purified product) total volume should be

between 30-40μL. Use loading dye accordingly (E.g. for 40μL use 4μL dye).

5. For only visualising the DNA band at ladder size

2μL of DNA + 1μL 10X FastDigest Green Buffer + 7μL 1X TBE buffer

0.5μL of ladder + 1μL 10X FastDigest Green Buffer + 8.5μL 1X TBE buffer

4.3. DNA extraction (Gel Purification)
a. Weigh a 1.5ml tube and note down the weight.
b. Excise the gel containing DNA band with a clean scalpel or razor and place

it in a 1.5ml tube. Cut as close to the DNA as possible to reduce gel volume.

c. Record the weight of the tube with gel.
d. Add 1:1 volume of binding buffer to the gel slice. For e.g. 100μL for 100mg

agarose gel.

e. Incubate the gel mixture at 50-60°C for 10minutes or until the gel slice

dissolves completely. Vortex the gel mixture briefly before loading it onto

the column.

f. Check the colour of the solution. The yellow colour indicates optimal pH for

DNA binding. If the colour of the solution is orange/violet add 10μL of 3M

sodium acetate (pH 5.2).

g. Transfer up to 800μL of solubilised gel solution to the purification column.
h. Centrifuge at 12,500 rpm for 1minute. Discard the flow through and place

the column back into the same tube.

i. Add 700μL of wash buffer to the purification column.

Table 6: TBE Buffer (5X) for 1litre

Tris base | 54g
Boric acid | 27.5g
0.5M EDTA (pH 8.0) | 20ml
pH | 8.3

j. Centrifuge at 12,500 rpm for 1minute. Discard the flow through and place

the column back into the same collection tube.

k. Centrifuge the empty purification column for an additional 1minute at

12,500rpm to remove any residual wash buffer.

l. Transfer the purification column to another 1.5ml microcentrifuge tube.
m. Add 30μL of nuclease-free water to the centre of the purification column and

incubate at 37°C for 2minutes. (Protocol: 50μL of elution buffer to the

centre of the purification column and centrifuge at 12,500rpm for 1 minute).

n. Centrifuge at 12,500 rpm for 2 minutes.
o. Discard the purification column and store the DNA at -20°C
p. Perform qualitative and quantitative analysis of DNA as mentioned in 2.1

using appropriate parameters.

For real-time detection, 50μM MB is to be added to the PCR mixture.

(Reference: Tseng, H. Y., Adamik, V., Parsons, J., Lan, S. S., Malfesi, S., Lum, J.,

... & Gray, B. (2014). Development of an electrochemical biosensor array for

quantitative polymerase chain reaction utilizing three-metal printed circuit board

technology. Sensors and Actuators B: Chemical, 204, 459-466).

Validation Parameters

End-point analysis ( (https://www.zotero.org/google-docs/?5f6piL)Guidelines for the Validation of Analytical Methods for

Nucleic Acid Sequence-Based Analysis of Food, Feed, Cosmetics and Veterinary

Products, (https://www.zotero.org/google-docs/?5f6piL) n.d.): (https://www.zotero.org/google-docs/?5f6piL)

a. Sensitivity (LOD): Perform serial dilutions for target DNA and 12 replicates for

each dilution level. Dilution with lowest copy number showing positive result

for all 12 replicates is the approximate value of LOD. It can be expressed as

concentration of DNA (ng or pg) or target copy number/reaction. Formula LOD

= 3.3σ /S (where σ is standard deviation and S is the slope of calibration curve)

b. False negative (FN)/False positive (FP): FN occurs if the test result if negative

but actual condition is positive (conc ≥ LOD); FP occurs when test result is

positive but actual condition is negative. FN and FP rates determined should be

<5%.

c. Robustness: It is the ability to remain unaffected by small deliberate deviations

from experimental conditions.

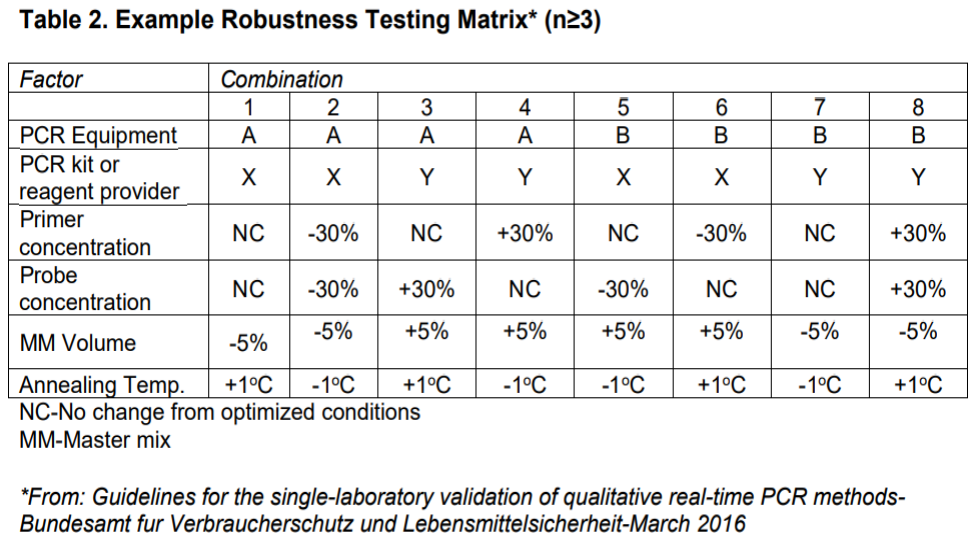
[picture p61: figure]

Reproducibility: Same DNA concentration amplified in replicates for both thermal

cyclers (Everardo Gonzalez-Gonzalez et.al)

PCR efficiency curve: Amplicon product concentration vs target DNA

concentration. Calculate R of curve fit and compare old and new thermal cyclers.

Real-time analysis

Standard curves: Generation of standard curves is required for optimization of PCR

results. Used for determination of PCR efficiency, dynamic range and LOQ.

PCR efficiency: Measure of how close the observed reaction is to statistical

doubling. Standard curve of Ct vs log of sample concentration, no. of template

copies or dilution factor with average slope between -3.1 to -3.6 with efficiency of

90%-110% generally acceptable. Slope (y) = mx + b (where y = CT value and x =

log target amount)
PCR efficiency (E) = (10⁻¹/m –1) x100, where E = efficiency and m = slope of the

linear standard curve.

Dynamic range: Concentration range over which target nucleic acid is reliably

detected. A well-designed and well-optimized real time PCR assay will have a linear range of 6-8 orders of magnitude. The R² value of the standard curves used

to determine the dynamic range should be ≥0.98.

Limit of quantification (LOQ): Lowest amount of analyte in a sample that can be

reliably quantified. LOQ = 10σ / S (where σ is standard deviation and S is the

slope of calibration curve)

Repeatability and Reproducibility Standard Deviation: RSDrepeatability is the relative

standard deviation of results obtained with the same method, by the same analyst,

in the same laboratory, with the same equipment, on the same samples

(repeatability conditions). Should be <25% over the whole dynamic range of the

assay. The relative standard deviation between laboratories (RSDreproducibility) should

be less than 35%.

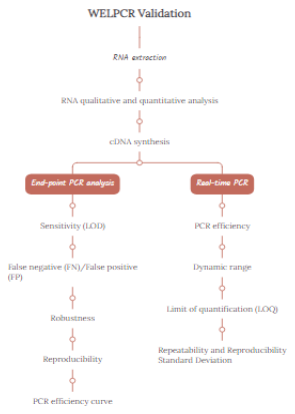
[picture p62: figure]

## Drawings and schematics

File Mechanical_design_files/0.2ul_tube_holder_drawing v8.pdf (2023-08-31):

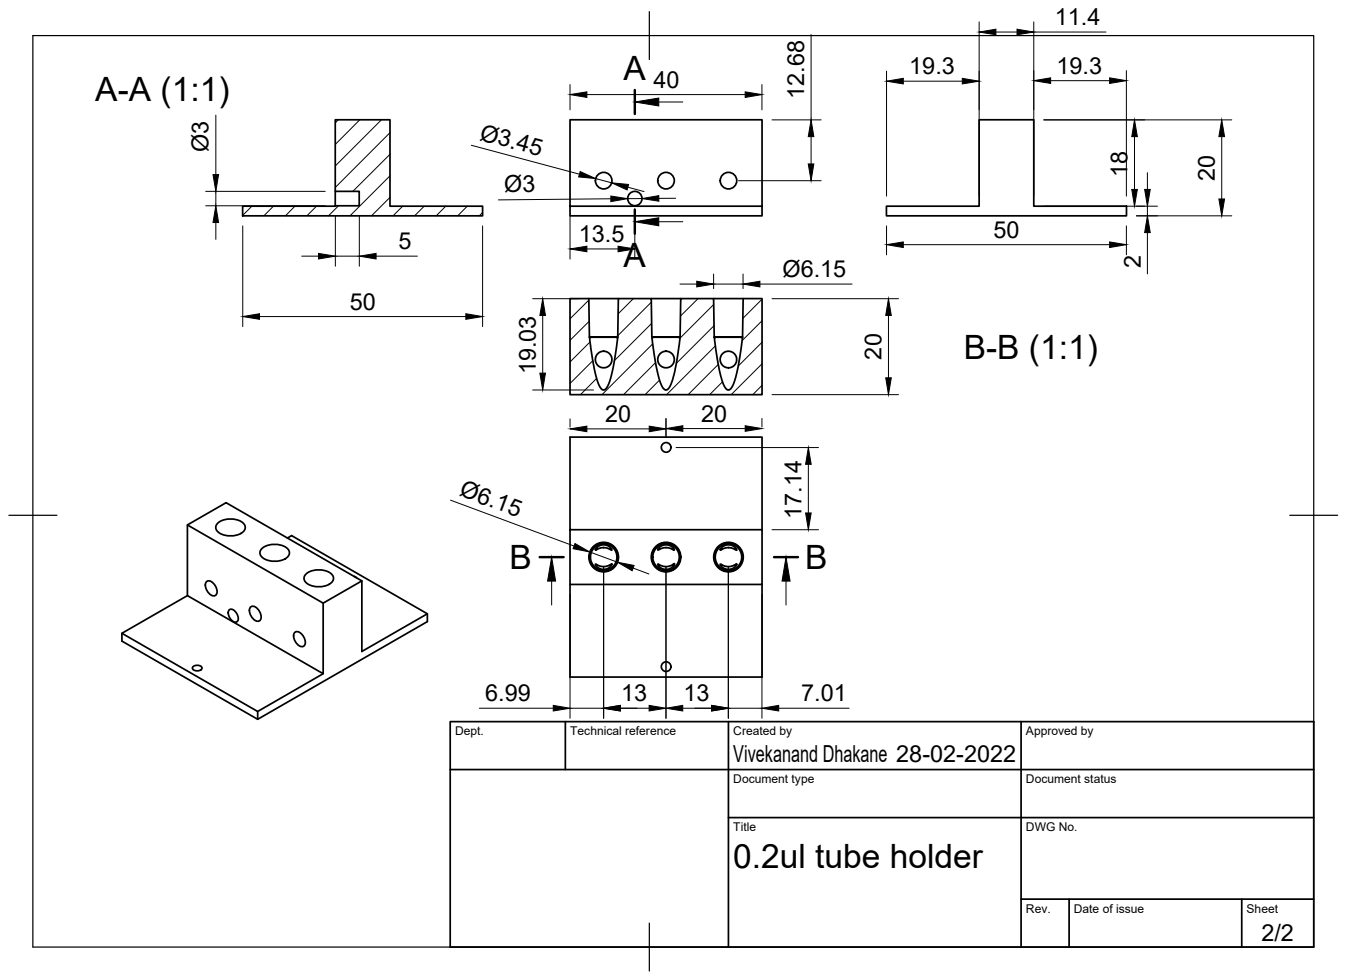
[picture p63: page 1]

Dept. | Technical reference | Created by Vivekanand Dhakane 28-02-2022 | Approved by

Document type | Document status

Title 0.2ul tube holder | DWG No.

Rev. | Date of issue | Sheet 2/2

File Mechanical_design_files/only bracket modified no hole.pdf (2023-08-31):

54

23:5

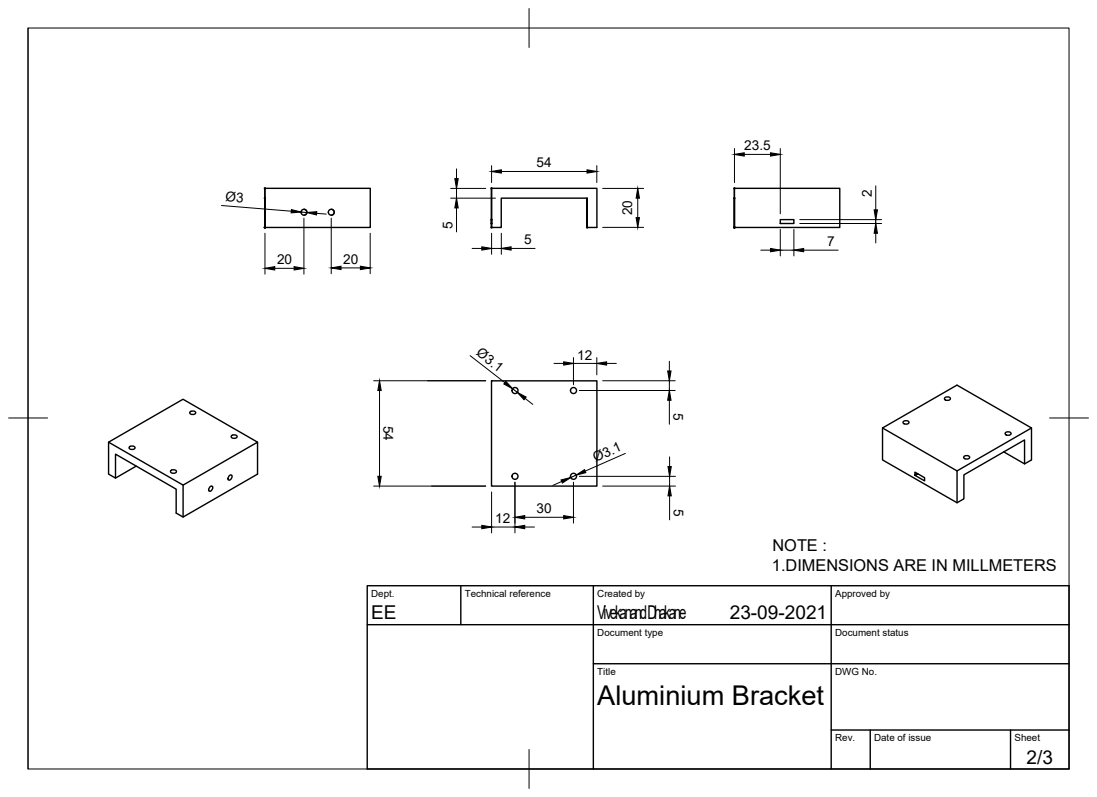
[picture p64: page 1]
Dept:; Technical reference; Created by; Approved by; VivekanandDhakane ²M

NOTE :
L:DIMENSIONS ARE IN MILLMETERS

Document type | Document status

Title Aluminium Bracket | DWG No:

Rev: | Date of issue | Sheet 2I3

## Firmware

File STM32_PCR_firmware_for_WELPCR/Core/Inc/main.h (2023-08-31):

/* USER CODE BEGIN Header */
/**
  ******************************************************************************
  * @file           : main.h
  * @brief          : Header for main.c file.
  *                   This file contains the common defines of the application.
  ******************************************************************************
  * @attention
  *
  * <h2><center>&copy; Copyright (c) 2021 STMicroelectronics.
  * All rights reserved.</center></h2>
  *
  * This software component is licensed by ST under BSD 3-Clause license,
  * the "License"; You may not use this file except in compliance with the
  * License. You may obtain a copy of the License at:
  *                        opensource.org/licenses/BSD-3-Clause
  *
  ******************************************************************************
  */
/* USER CODE END Header */

/* Define to prevent recursive inclusion -------------------------------------*/
#ifndef __MAIN_H
#define __MAIN_H

#ifdef __cplusplus
extern "C" {
#endif

/* Includes ------------------------------------------------------------------*/
#include "stm32f1xx_hal.h"

/* Private includes ----------------------------------------------------------*/
/* USER CODE BEGIN Includes */

/* USER CODE END Includes */

/* Exported types ------------------------------------------------------------*/
/* USER CODE BEGIN ET */




/* USER CODE END ET */

/* Exported constants --------------------------------------------------------*/
/* USER CODE BEGIN EC */

/* USER CODE END EC */

/* Exported macro ------------------------------------------------------------*/
/* USER CODE BEGIN EM */

/* USER CODE END EM */

void HAL_TIM_MspPostInit(TIM_HandleTypeDef *htim);

/* Exported functions prototypes ---------------------------------------------*/
void Error_Handler(void);

/* USER CODE BEGIN EFP */










/* USER CODE END EFP */

/* Private defines -----------------------------------------------------------*/
#define LCD_CS_Pin GPIO_PIN_14
#define LCD_CS_GPIO_Port GPIOC
#define BUZZER_Pin GPIO_PIN_4
#define BUZZER_GPIO_Port GPIOA
#define J_UP_Pin GPIO_PIN_0
#define J_UP_GPIO_Port GPIOB
#define J_DOWN_Pin GPIO_PIN_1
#define J_DOWN_GPIO_Port GPIOB
#define LCD_DC_Pin GPIO_PIN_2
#define LCD_DC_GPIO_Port GPIOB
#define J_LEFT_Pin GPIO_PIN_10
#define J_LEFT_GPIO_Port GPIOB
#define J_RIGHT_Pin GPIO_PIN_11
#define J_RIGHT_GPIO_Port GPIOB
#define J_MID_Pin GPIO_PIN_12
#define J_MID_GPIO_Port GPIOB
#define J_SET_Pin GPIO_PIN_13
#define J_SET_GPIO_Port GPIOB
#define J_RST_Pin GPIO_PIN_14
#define J_RST_GPIO_Port GPIOB
#define BLOCK_PWM_1_Pin GPIO_PIN_8
#define BLOCK_PWM_1_GPIO_Port GPIOA
#define BLOCK_PWM_2_Pin GPIO_PIN_9
#define BLOCK_PWM_2_GPIO_Port GPIOA
#define LID_PWM_Pin GPIO_PIN_10
#define LID_PWM_GPIO_Port GPIOA
#define TOUCH_CS_Pin GPIO_PIN_3
#define TOUCH_CS_GPIO_Port GPIOB
#define STATUS_LED_Pin GPIO_PIN_4
#define STATUS_LED_GPIO_Port GPIOB
#define LCD_RESET_Pin GPIO_PIN_5
#define LCD_RESET_GPIO_Port GPIOB
#define TOUCH_IRQ_Pin GPIO_PIN_8
#define TOUCH_IRQ_GPIO_Port GPIOB
/* USER CODE BEGIN Private defines */

/* USER CODE END Private defines */

#ifdef __cplusplus
}
#endif

#endif /* __MAIN_H */

/************************ (C) COPYRIGHT STMicroelectronics *****END OF FILE****/

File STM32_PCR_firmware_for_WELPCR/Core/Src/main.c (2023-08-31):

/* USER CODE BEGIN Header */
/**
  ******************************************************************************
  * @file           : main.c
  * @brief          : Main program body
  ******************************************************************************
  * @attention
  *
  * <h2><center>&copy; Copyright (c) 2021 STMicroelectronics.
  * All rights reserved.</center></h2>
  *
  * This software component is licensed by ST under BSD 3-Clause license,
  * the "License"; You may not use this file except in compliance with the
  * License. You may obtain a copy of the License at:
  *                        opensource.org/licenses/BSD-3-Clause
  *
  ******************************************************************************
  */
/* USER CODE END Header */
/* Includes ------------------------------------------------------------------*/
#include "main.h"

/* Private includes ----------------------------------------------------------*/
/* USER CODE BEGIN Includes */
#pragma GCC push_options    /*It turns on certain optimization flags for GCC*/
#pragma GCC optimize ("Os")


#include "fonts.h"
#include "ssd1306.h"
#include "test.h"
#include "math.h"
#include "OLED_GUI.h"
#include "5D_joystick.h"
#include "thermister_10k.h"
#include "thermocycler.h"
#include "PID.h"
#include "thermistor.h"
#pragma GCC pop_options

#include "ILI9341_STM32_Driver.h"
#include "ILI9341_GFX.h"
/* USER CODE END Includes */

/* Private typedef -----------------------------------------------------------*/
/* USER CODE BEGIN PTD */

/* USER CODE END PTD */

/* Private define ------------------------------------------------------------*/
/* USER CODE BEGIN PD */
/* USER CODE END PD */

/* Private macro -------------------------------------------------------------*/
/* USER CODE BEGIN PM */
#define BLOCK_DUTY_HIGHEST        100
#define BLOCK_HIGHEST_TEMP_DIFF   20
#define BLOCK_PID_P               (float)((float)BLOCK_DUTY_HIGHEST/(float)BLOCK_HIGHEST_TEMP_DIFF)
#define ABS(x)                    ((x) > 0? (x) :-(x) )
#define BLOCK_TEMPERATURE_PIN     ADC_CHANNEL_1
#define LID_TEMPERATURE_PIN       ADC_CHANNEL_0
#define EXTRA_TEMPERATURE_PIN_1     ADC_CHANNEL_2
#define EXTRA_TEMPERATURE_PIN_2    ADC_CHANNEL_3

/* Controller parameters */
/*
#define PID_KP  0.0f
#define PID_KI  0.0f      //0.5f
#define PID_KD  0.0f      //0.25f
*/


#define LID_PID_KP       		40.0f
#define LID_PID_KI       		1.3333f      //0.5f
#define LID_PID_KD       		300.0f       //0.25f
#define LID_PID_TAU      		0.02f	     //36
#define LID_PID_LIM_MIN  		0.0f
#define LID_PID_LIM_MAX  		100.0f
#define LID_PID_LIM_MIN_INT  	0.0f
#define LID_PID_LIM_MAX_INT  	500.0f
#define LID_SAMPLE_TIME_S 		0.1f
#define LID_PID_BETA 		        0.0f

#define LID_PWM_MAX  		999.0f


#define PELTIER_PID_KP   		  5.0f //40
#define PELTIER_PID_KI   		  0.0f      //0.5f
#define PELTIER_PID_KD   		  0.0f      //0.25f
#define PELTIER_PID_TAU 		  15.0f
#define PELTIER_PID_LIM_MAX  	  999
#define PELTIER_PID_LIM_MIN  	  (-999)
#define PELTIER_PID_LIM_MIN_INT   (-450)
#define PELTIER_PID_LIM_MAX_INT   (450)
#define PELTIER_SAMPLE_TIME_S 	  0.1f
#define PELTIER_PID_BETA 	       0.0f
#define PELTIER_NO_OF_SAMPLES_AVG  5


/*
 *
#define PCR1

#ifdef PCR1

Defines for PCR 1

#endif /* PCR1*/

/*
#ifdef PCR2

Defines for PCR 2

#endif /* PCR2*/





//PCR1
#define BLOCK_THERMISTOR_R0			(float)10261//11194//10698//9750
#define BLOCK_THERMISTOR_RS			(float)998//990
#define BLOCK_THERMISTOR_ADC        &hadc1
#define BLOCK_THERMISTOR_CHANNEL    ADC_CHANNEL_1
#define BLOCK_THERMISTOR_BETA       (float)4047//3609//3495//3182

#define EXTRA_1_THERMISTOR_R0		  (float)5097
#define EXTRA_1_THERMISTOR_RS		  (float)975.0
#define EXTRA_1_THERMISTOR_ADC        &hadc1
#define EXTRA_1_THERMISTOR_CHANNEL    ADC_CHANNEL_2
#define EXTRA_1_THERMISTOR_BETA       (float)3838


#define EXTRA_2_THERMISTOR_R0		  (float)5097
#define EXTRA_2_THERMISTOR_RS		  (float)977.0
#define EXTRA_2_THERMISTOR_ADC        &hadc1
#define EXTRA_2_THERMISTOR_CHANNEL    ADC_CHANNEL_3
#define EXTRA_2_THERMISTOR_BETA       (float)3838




/* USER CODE END PM */

/* Private variables ---------------------------------------------------------*/
ADC_HandleTypeDef hadc1;

I2C_HandleTypeDef hi2c1;

SPI_HandleTypeDef hspi1;
DMA_HandleTypeDef hdma_spi1_tx;

TIM_HandleTypeDef htim1;
TIM_HandleTypeDef htim2;

PCD_HandleTypeDef hpcd_USB_FS;

/* USER CODE BEGIN PV */

char num_string[10];
float block_cur_temp,IIR_block_cur_temp,block_cur_error,block_pre_out;
float block_set_temp = 35;
int block_PWM ;
volatile uint8_t OLED_lock = 0;
uint8_t joystick_out;
PCR_settings_t* PCR_settings;
float set_point;
parameter* annealing_temp;
float lid_cur_temp,Lid_setpoint = 100;
int lid_pwm_count;

float dummy_p,dummy_I,dummy_D,Peltier_PWM_beta;
float PELTIER_PID_WINDOW = 2.0f;
float PELTIER_PID_SMALL_WINDOW = 2.0f;
float PELTIER_TEMP_IIR_ALFA  =    0.9;
float extra_temperature_2      = 0;
float extra_temperature_1      = 0;
uint8_t peltier_PID_state = 0;
int16_t x_pos;
int16_t y_pos;
volatile uint8_t update_live = 0;

int current_PWM = 0;


/* USER CODE END PV */

/* Private function prototypes -----------------------------------------------*/
void SystemClock_Config(void);
static void MX_GPIO_Init(void);
static void MX_DMA_Init(void);
static void MX_TIM1_Init(void);
static void MX_ADC1_Init(void);
static void MX_I2C1_Init(void);
static void MX_TIM2_Init(void);
static void MX_SPI1_Init(void);
static void MX_USB_PCD_Init(void);
/* USER CODE BEGIN PFP */

//float get_heat_block_temperature_LM35_A0(void);
//float get_heat_block_temperature_10k_thermistor_A1(void);
void Display_temperature(float num);
/* USER CODE END PFP */

/* Private user code ---------------------------------------------------------*/
/* USER CODE BEGIN 0 */

/* USER CODE END 0 */

/**
  * @brief  The application entry point.
  * @retval int
  */
int main(void)
{
  /* USER CODE BEGIN 1 */


  /* USER CODE END 1 */

  /* MCU Configuration--------------------------------------------------------*/

  /* Reset of all peripherals, Initializes the Flash interface and the Systick. */
  HAL_Init();

  /* USER CODE BEGIN Init */

  /* USER CODE END Init */

  /* Configure the system clock */
  SystemClock_Config();

  /* USER CODE BEGIN SysInit */

  /* USER CODE END SysInit */

  /* Initialize all configured peripherals */
  MX_GPIO_Init();
  MX_DMA_Init();
  MX_TIM1_Init();
  MX_ADC1_Init();
  MX_I2C1_Init();
  MX_TIM2_Init();
  MX_SPI1_Init();
  MX_USB_PCD_Init();
  /* USER CODE BEGIN 2 */

  ILI9341_Init();
  ILI9341_FillScreen(BLACK);
  ILI9341_SetRotation(SCREEN_HORIZONTAL_2);
  //ILI9341_DrawText("HELLO WORLD", FONT4, 0, 200, YELLOW, BLACK);
  //ILI9341_DrawPixel(160,120,RED);

  float temp =0.5;
  float pre_block_cur_temp;

  HAL_Delay(100);
  //SSD1306_Init();  // initialise

  TIM1->CCR1 = 0;
  TIM1->CCR2 = 0;


  Device_start_buzzer();
  display_big_message("WELPCR", "----tagline----",big_font,2);
  //OLED_PCR_config_GUI_init();

  /*SSD1306_GotoXY (0,0);
  SSD1306_Puts ("WELPCR", &Font_11x18, 1);
  SSD1306_UpdateScreen(); //display*/
  //HAL_Delay(1000);
  //SSD1306_Clear();
  get_PCR_settings(&PCR_settings);
  annealing_temp = (*PCR_settings).annealing_temp;










  block_cur_temp = get_thermister_temp(&hadc1, BLOCK_TEMPERATURE_PIN);

  //start_thermocycler();


  PIDController LID_pid = { LID_PID_KP, LID_PID_KI, LID_PID_KD,
	                    LID_PID_TAU,
	                    LID_PID_LIM_MIN, LID_PID_LIM_MAX,
	                    LID_PID_LIM_MIN_INT,
	                    LID_PID_LIM_MAX_INT,
	                    LID_SAMPLE_TIME_S,
						LID_PID_BETA
  	  	  	  	  	  };

   PIDController_Init(&LID_pid);

   PIDController peltier_pid = { PELTIER_PID_KP, PELTIER_PID_KI, PELTIER_PID_KD,
		   	   	   	    PELTIER_PID_TAU,
						PELTIER_PID_LIM_MIN, PELTIER_PID_LIM_MAX,
						PELTIER_PID_LIM_MIN_INT,
						PELTIER_PID_LIM_MAX_INT,
						PELTIER_SAMPLE_TIME_S,
						PELTIER_PID_BETA
   	  	  	  	  	  };

    PIDController_Init(&peltier_pid);


    thermistor_t block_thermistor ={
       					BLOCK_THERMISTOR_R0,
   						BLOCK_THERMISTOR_RS,
   						BLOCK_THERMISTOR_BETA,
   						BLOCK_THERMISTOR_ADC,
   						BLOCK_THERMISTOR_CHANNEL
       					};

    thermistor_t EXTRA_thermistor_1 ={
       						EXTRA_1_THERMISTOR_R0,
   							EXTRA_1_THERMISTOR_RS,
   							EXTRA_1_THERMISTOR_BETA,
   							EXTRA_1_THERMISTOR_ADC,
   							EXTRA_1_THERMISTOR_CHANNEL
           					};

     thermistor_t EXTRA_thermistor_2 ={
       		                EXTRA_2_THERMISTOR_R0,
   							EXTRA_2_THERMISTOR_RS,
   							EXTRA_2_THERMISTOR_BETA,
   							EXTRA_2_THERMISTOR_ADC,
   							EXTRA_2_THERMISTOR_CHANNEL
           					};

     thermistor_t LID_thermistor ={
               					BLOCK_THERMISTOR_R0,
           						BLOCK_THERMISTOR_RS,
           						BLOCK_THERMISTOR_BETA,
           						BLOCK_THERMISTOR_ADC,
   								LID_TEMPERATURE_PIN
               					};






   TIM1->CCR3 =lid_pwm_count;



   HAL_TIM_PWM_Start(&htim1, TIM_CHANNEL_3);





  HAL_TIM_Base_Start_IT(&htim2);










  /* USER CODE END 2 */

  /* Infinite loop */
  /* USER CODE BEGIN WHILE */
  while (1)
  {
    /* USER CODE END WHILE */

    /* USER CODE BEGIN 3 */

	  /*-------------Extra temperature------------*/


	  get_thermistor_temp_(&EXTRA_thermistor_1);
	   extra_temperature_1 =EXTRA_thermistor_1.temperature;
	  get_thermistor_temp_(&EXTRA_thermistor_2);
	  extra_temperature_2 =EXTRA_thermistor_2.temperature;

	//----------------------------------------------------------

	  update_GUI();

	  check_touch();

	  /*---calulate temperature and add IIR filter*/
	  //pre_block_cur_temp = block_cur_temp;
	  float avg_block_cur_temp_1 = 10;
	  float avg_block_cur_temp_2 = 0;
	  float small_window_kp;
	  while (ABS(avg_block_cur_temp_1 - avg_block_cur_temp_2) > 0.5)
	  {
		  avg_block_cur_temp_1 = 0;
		  avg_block_cur_temp_2 = 0;
		  for (int i=0; i< PELTIER_NO_OF_SAMPLES_AVG; i++)
		  	  {
			  	  	  get_thermistor_temp_(&block_thermistor);
			  		  avg_block_cur_temp_1 +=  block_thermistor.temperature/ PELTIER_NO_OF_SAMPLES_AVG;
		  	  }
		  for (int i=0; i< PELTIER_NO_OF_SAMPLES_AVG; i++)
		  	  {
			  	  	  get_thermistor_temp_(&block_thermistor);
			  		  avg_block_cur_temp_2 += block_thermistor.temperature/ PELTIER_NO_OF_SAMPLES_AVG;
		  	  }

	  }

	/*  if(ABS(pre_block_cur_temp- avg_block_cur_temp) >0)
	  {

		  block_cur_temp = pre_block_cur_temp;
	  }
	  else
	  {
		  block_cur_temp =avg_block_cur_temp;
	  }
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
